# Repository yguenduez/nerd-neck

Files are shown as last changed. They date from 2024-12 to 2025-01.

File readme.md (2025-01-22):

# Nerd Neck on ESP32-S3

This small device will detect bad posture, if the person wearing this device has it attached to the back.

## Project structure

- [3dprint](3dprint): STL-Files for printing
- [images](images): All images used in the report or in this readme
- [nerd-neck](nerd-neck): Source code: Entry point for the program
- [utility](utility): Source code: Utility functions and the madgwick adapter
- [nerd-neck-report](nerd-neck-report): The [mdbook](https://github.com/rust-lang/mdBook) to render the report to pdf

## Outline

We read IMU data in a cycle. Every 50 milliseconds we receive IMU data.
As the IMU values drift, we need a filter(s): Those correct the drift integrated over time with sensor fusion
algorithms.

If the orientation of the device passes a certain threshold,
the device will start beeping for 2 seconds, notifying the person to rectify its position.
It will remain beeping, until the person corrected its position.

The whole device is a wearable, so it needs a battery (LiPo) and a 3d printed casing.

## TODOs

- [x] Calculate an angle to Z-Axis (with Filters), that can be used as "beep" input
- [x] ~~Do a calibration for the Gyro before starting (if not moving, gyro values should be 0).~~ (Filter already
  corrects offsets)
- [x] Write a little rust driver for the speaker, that controls it
- [x] On a configurable threshold - enable the trigger for the beep speaker
- [x] Apply a LiPo (3.7 Volts) battery adapter to the battery pins
- [x] Design 3d model for the casing to print
- [x] Print the casing
- [x] Assemble the parts
- [x] Write Report with Markdown
- [x] Slides with UniBas flavour

## IMU Drift

Gyroscope does drift, when integrated over time, so we need to correct those values with sensor fusion algorithms,
with other sensor values. Both IMUs we can use, also come with an accelerometer.
So we combine smooth short-them gyroscope data with long-term stability of accelerometer data.

Possible Filters:

- **Complementary filter** (simpler but effective for many use cases).
- **Madgwick filter** (a fast, quaternion-based algorithm for IMUs).
- **Mahony filter** (similar to Madgwick with some differences in accuracy and computation).
- **Kalman filter** (complex but precise, especially for combining multiple sensors).

**Note**: As we are only interested in the tilt of the IMU (diff angle to the vertical z-axis), we can neglect
the yaw angle (which would be corrected be the magnetometer, which we do not have).

So we can use either Madgwick or Mahony with only given accelerometer and gyro values.

### IMU Filter Implementation

There is already a [third party crate (ahrs-rs)](https://github.com/jmagnuson/ahrs-rs), that already implements both
Madgwick and Mahony filters
for both 6DoF and 9DoF IMUs.

A choice to be done is the filter gains, KI and KP for Mahony and Beta for Madgwick.

Some recommended beta values for the Madgwick Filter, where you have to choose
between responsiveness and stability:

| Drones/RC vehicles    | 0.1 - 0.3    | High dynamics, prioritize responsiveness.            |
|-----------------------|--------------|------------------------------------------------------|
| Robotics (general)    | 0.05 - 0.2   | Moderate dynamics, balance response and drift.       |
| Slow-motion systems   | 0.01 - 0.05  | Low dynamics, prioritize stability/noise rejection.  |
| Human motion tracking | 0.01 - 0.1   | Prioritize stability but allow small dynamic motion. |
| Static applications   | 0.001 - 0.01 | Low dynamics, focus on maximum stability.            |

TL;DR: We use the Madgwick filter with beta between 0.01 and 0.1. Currently, we use 0.1.
The paper for madgwick is [here](https://x-io.co.uk/downloads/madgwick_internal_report.pdf).

The Madgwick Feedback loop (from paper above):

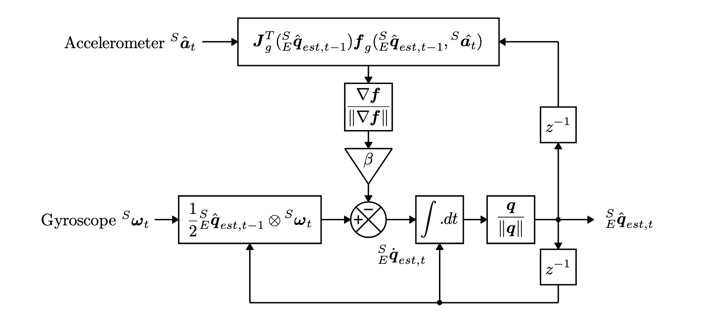
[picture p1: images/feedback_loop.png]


## IMU Sensors

We have several IMU Sensors

- [BMI160](https://www.dfrobot.com/product-1716.html)
- [MPU6050](https://learn.adafruit.com/mpu6050-6-dof-accelerometer-and-gyro/arduino)

Both can be addressed via a I2C-Bus.

## Software for the MPU6050

There is already a [MPU6050 crate](https://docs.rs/mpu6050/0.1.6/mpu6050/). It's usable with i2c.

## Software for the BMI160

There is already a [BMI160 create](https://docs.rs/bmi160/1.1.0/bmi160/). Also usable with i2c.

## I2C interface

This bus comes with a dataline (sda) and a line for the clock signal (scl).

You can connect several devices to the bus, like shown below.
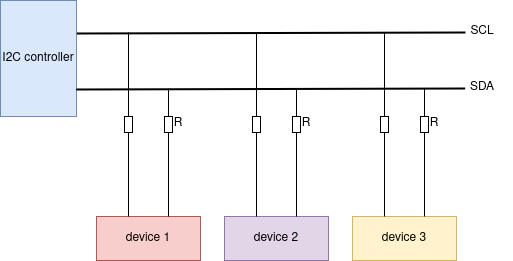
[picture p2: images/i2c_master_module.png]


Note from [espressif](https://docs.espressif.com/projects/esp-idf/en/v5.3.2/esp32s3/api-reference/peripherals/i2c.html):

> The frequency of SCL is influenced by both the pull-up resistor and the wire capacitance. Therefore, users are
> strongly recommended to choose appropriate pull-up resistors to make the frequency accurate. The recommended value for
> pull-up resistors usually ranges from 1K Ohms to 10K Ohms.
> Keep in mind that the higher the frequency, the smaller the pull-up resistor should be (but not less than 1 KOhms).
> Indeed, large resistors will decline the current, which will increase the clock switching time and reduce the
> frequency.
> We usually recommend a range of 2 KOhms to 5 KOhms, but users may also need to make some adjustments depending on
> their
> current draw requirements.

**TL;DR**: Use 2-10kOhm resistors as pull up resistors.
The higher the frequency, the lower the ohmage should be.

We use 4.7k Ohms as pull-up resistors.

## Pinouts of esp32s3 from Seeed

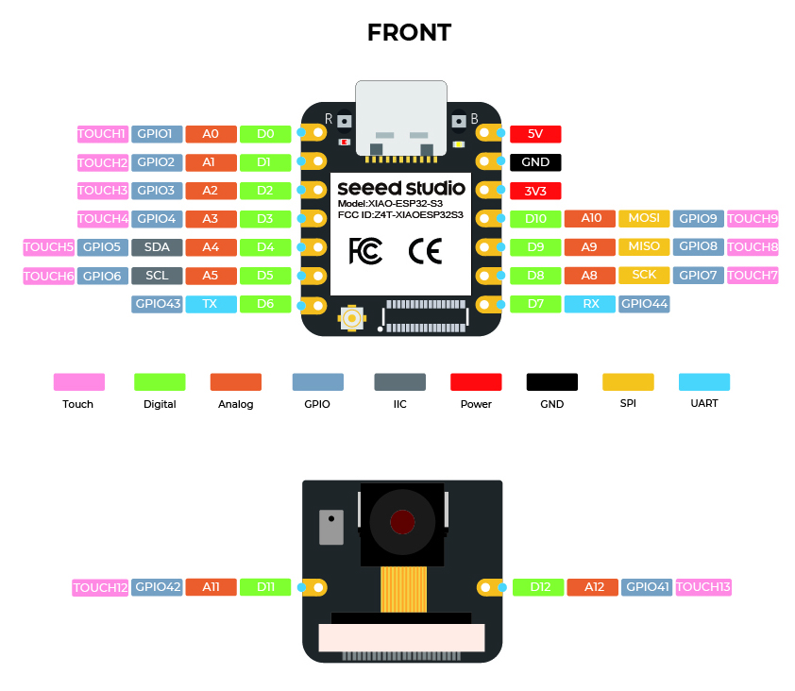
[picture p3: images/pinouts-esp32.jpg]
Pinouts


## Current Wiring

We have an i2c setup, where two 4.7k Ohm resistors are used as
pull up resistors. If scl/sda are off, both signals are pulled up to the logical 3.3 Volts (high). The IMU (on the
right)
will pull the signal down if needed.

Everything runs on the 3.3-volt level of the MCU.

The piezo speaker is connected to GPIO pin 7.
We use a 100 Ohms resistor to protect the GPIO from draining too much current.
So the piezo speaker drains at max 3.3v/100 Ohms = 33 mA of current.
It's powered with a 1 khz pwm signal, when triggered.

Below the fritzing image is demonstrating the wiring.
The parts are aliases though, we use different ones,
but the wiring is exactly the same.

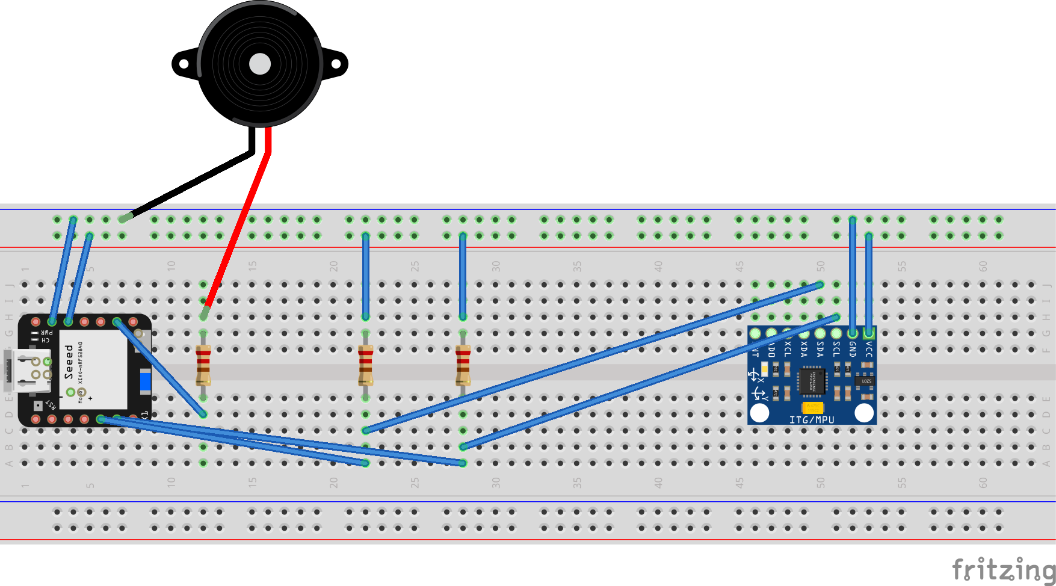
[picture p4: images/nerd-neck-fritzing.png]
fritzing


## Bill of Materials

Below all used Materials

### For the Breadboard Version

- MCU: Seeed xiao esp32s3, [link](https://wiki.seeedstudio.com/xiao_esp32s3_getting_started/)
- IMU: DF Robot BMI160 (6 DoF-IMU), [link](https://www.dfrobot.com/product-1716.html)
- 2x 4.7k Ohm Resistors as pull up resistors for the I2C connection
- 1x 100 Ohm Resistor for the piezo speaker
- Breadboard
- Active Piezo
  Buzzer, [link](https://www.bastelgarage.ch/piezo-buzzer-summer-aktiv?search=Piezo%20Buzzer%20Summer%20aktiv)
- Wires

### The Assembled (Battery powered Version)

- MCU: Seeed xiao esp32s3, [link](https://wiki.seeedstudio.com/xiao_esp32s3_getting_started/)
- IMU: DF Robot BMI160 (6 DoF-IMU), [link](https://www.dfrobot.com/product-1716.html)
- 2x 4.7k Ohm Resistors as pull up resistors for the I2C connection
- 1x 100 Ohm Resistor for the piezo speaker
- Active Piezo
  Buzzer, [link](https://www.bastelgarage.ch/piezo-buzzer-summer-aktiv?search=Piezo%20Buzzer%20Summer%20aktiv)
- Wires
- Battery: LiPo, 3.7 volts with
  1500mAh: [link](https://www.bastelgarage.ch/lipo-akku-1500mah-jst-2-0-lithium-ion-polymer?search=LiPo%20Akku%201500mAh%20JST%202.0%20%2F%20Lithium%20Ion%20Polymer)
- JST-PH crimp plugs and sockets (To not directly solder the battery to the
  MCU), [link](https://www.bastelgarage.ch/jst-ph-crimp-stecker-und-buchsen-2mm-set-40-stuck)

## Building and flashing

### Prerequisites

Install all the depenendencies:

- Install [Rust](https://www.rust-lang.org/tools/install)
- Install esp tooling
    - `cargo install espup espflash`
    - `espup install`

### Building/Flashing

Then go into the `nerd-neck` directory and
`source ~/export-esp.h` (generated from `espup install`).

To build and flash the firmware to the device,
just run `cargo run --release`.

# Casing

## Requirements

The casing must include

- a LiPo battery (3.7 Volts),
  e.g. [this one](https://www.bastelgarage.ch/lipo-akku-1500mah-jst-2-0-lithium-ion-polymer?search=lipo) (52x42x5mm),
- the BMI160 IMU from DFRobots with dimensions 23x27mm as well as the
- the esp32s3 from seeed with dimensions ~20x25mm. Also having access to its usb-c port.
- the piezo buzzer with its dimensions, e.g. [this one](https://www.bastelgarage.ch/piezo-buzzer-summer-aktiv) (12mm)

As the casing will be quite flat, we have on one layer the flat LiPo battery on the bottom
and on the other layer the IMU, the MCU and the piezo buzzer. The wiring will be in between
those two.

Also: It should be possible to exchange all parts.

The casing will have the dimension of 56x46x10mm, so we
have a will thickness of 1mm on each side.

## Designs with Freecad

All below versions were designed with [FreeCad](https://www.freecad.org/), an open-source
CAD Software running on all major platforms (Mac, Linux and Windows).

### Version 0.1

The first design looks like this:

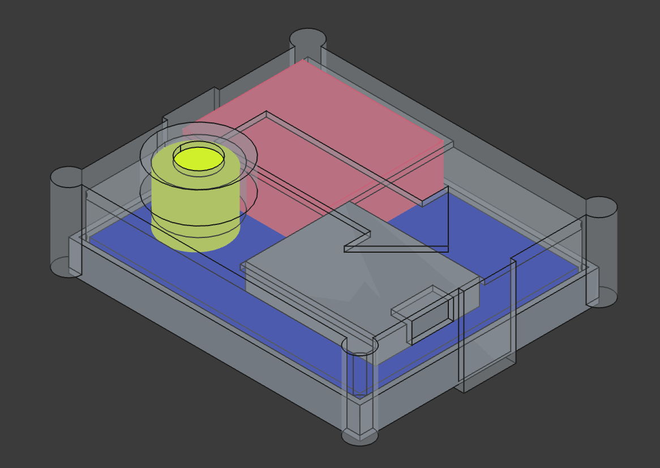
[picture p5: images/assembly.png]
assembly


Where the parts are the following:

- Red: the IMU
- Grey: Esp32s3
- Yellow: Piezo speaker
- Blue: the LiPo battery

The casing itself consists of a bottom and a top casing.
The bottom casing houses the battery.
The top casing holds the rest. Both parts are designed that way, that the
bottom half slips into the top half and snaps in.

The whole casing has the following dimensions: 56x46x15mm (circle on top for the buzzer has hight of 6mm)

### Version 0.2

Changes to V0.1:

- To make the design more 3D-print friendly, there is no exterior for the buzzer any more.
  The downside is,
  the buzzer is exposed a bit.
- The hole for the usb got bigger, as it did not go through without drilling.
- The two holders, that hold the bottom part, got 1mm longer, as the bottom part did not fit in.

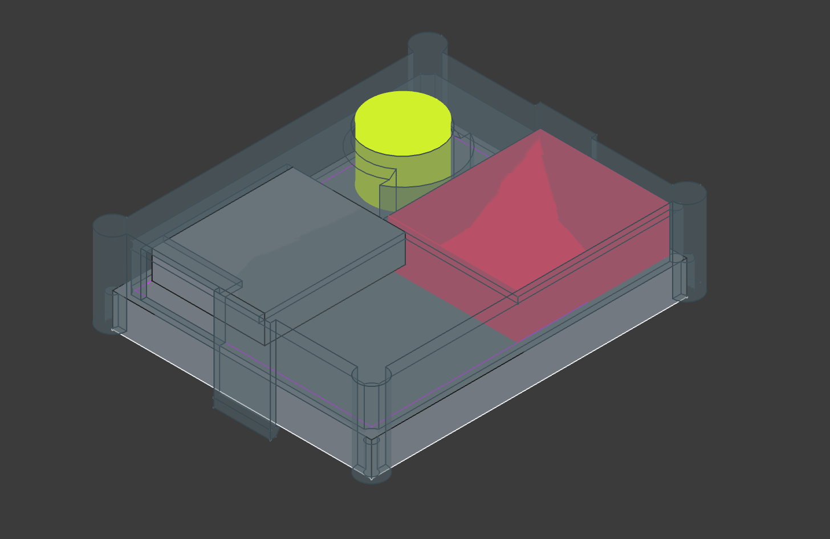
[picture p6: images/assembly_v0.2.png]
assmbly


### Version 0.3

Changes to V0.2:

- We thickened the holders by increasing their thickness from 1 mm to 2 mm.
- We resized the hole for the usb-c port.
- Decrease the height of the piezo buzzer holder, as the battery would not fit
- Decrease diameter of piezo buzzer hole from 13 mm to 12.3 mm

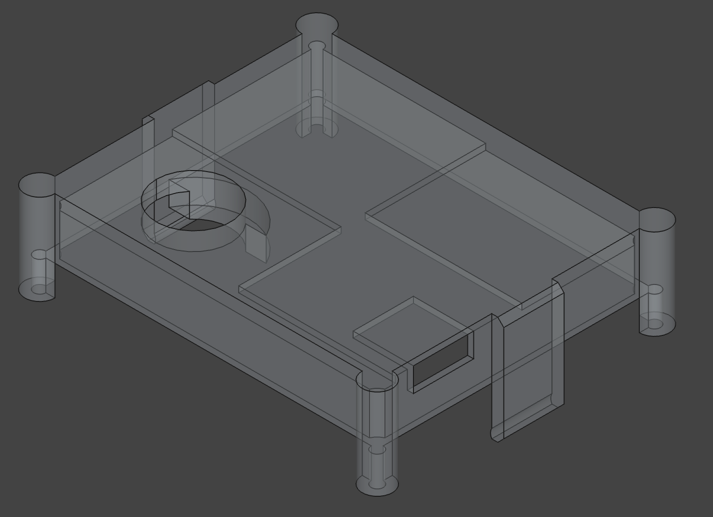
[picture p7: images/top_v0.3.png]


### Version 0.4

Changes to V0.3:

Instead of having a top and a bottom, the bottom part can now slide into the top part.
As such, we do not need any clips, to hold the bottom port. Only with gravity
the casing holds. The bottom part must be attached to a t-shirt in the end, as this will
hold the complete construction.

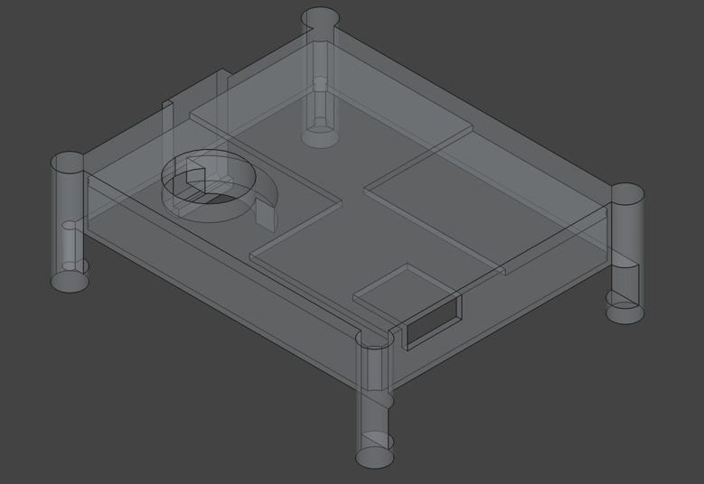
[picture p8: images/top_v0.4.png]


### Press-fit (Version 0.5)

Instead of sliding and clipping, we also tried a pressfit version.
The basic idea is that both parts, you want to connect do not perfectly fit to one another.
Instead they have an overlay, so you have to press them into each other.

The shear friction between those parts is enough, so they stick together.

The obvious pros. The parts are much easier to design, as you can see below (and compare them with the previous version)

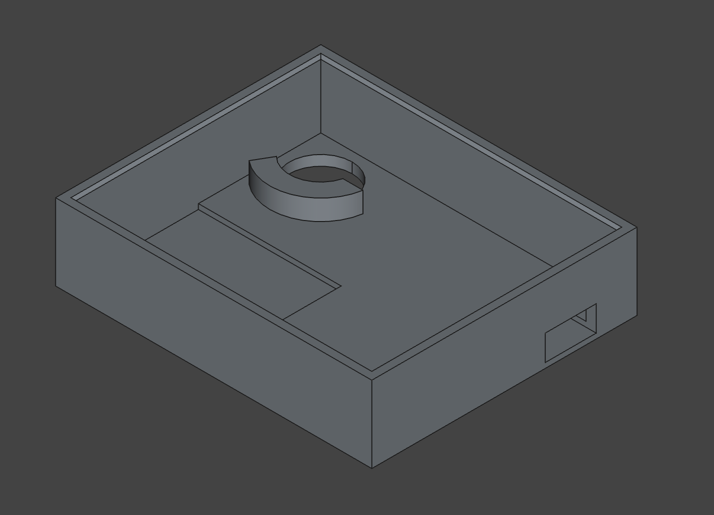
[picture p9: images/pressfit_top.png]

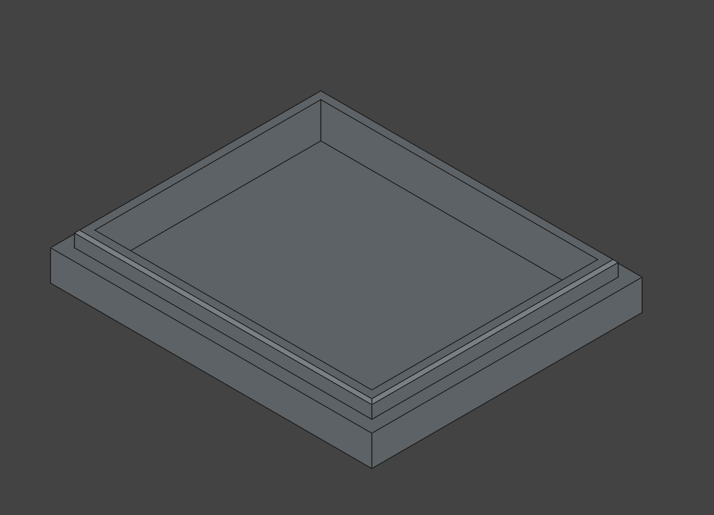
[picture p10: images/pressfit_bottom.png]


## The press fit is the final version

Printed, it looks like this:

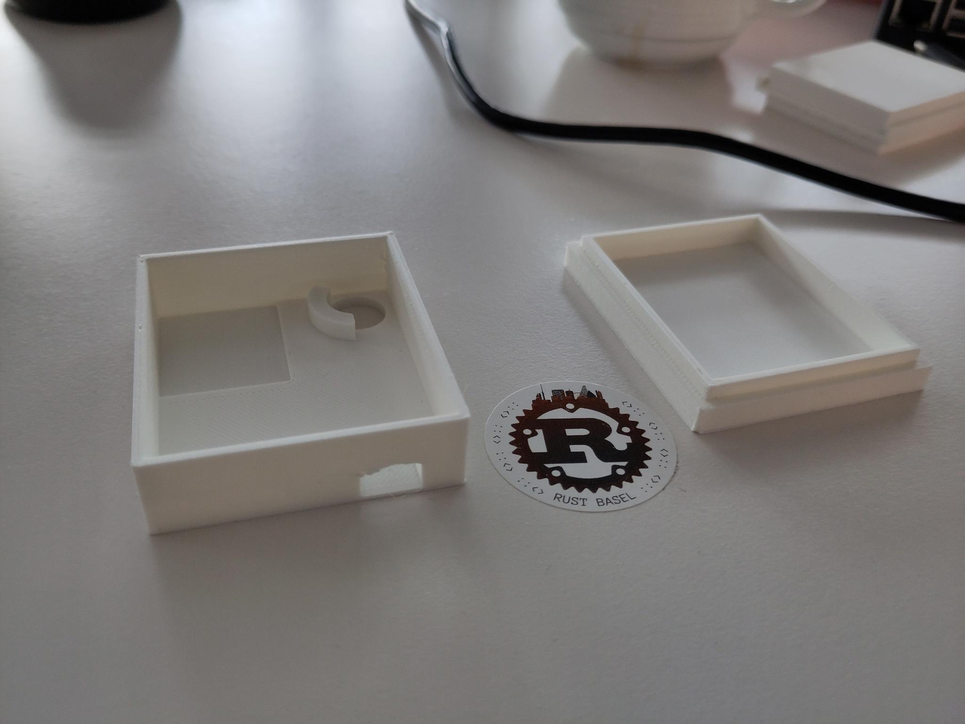
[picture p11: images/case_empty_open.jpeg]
casing_open

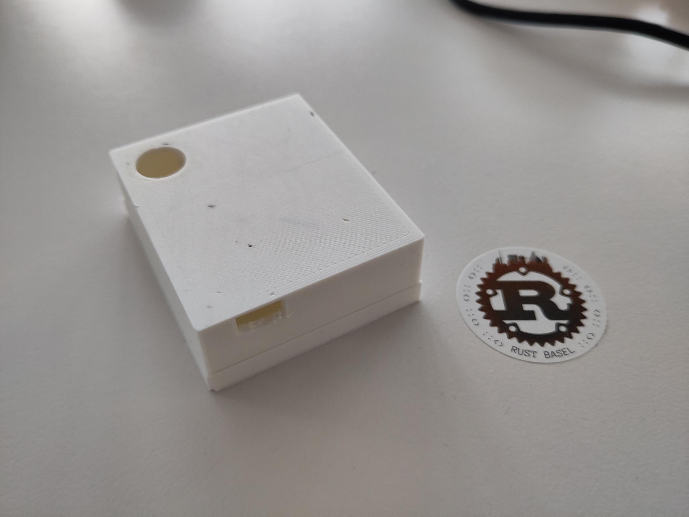
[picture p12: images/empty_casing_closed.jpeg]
casing_open


# Assembled Prototype

Below images of the assembled prototype, case opened and case closed

Opened:

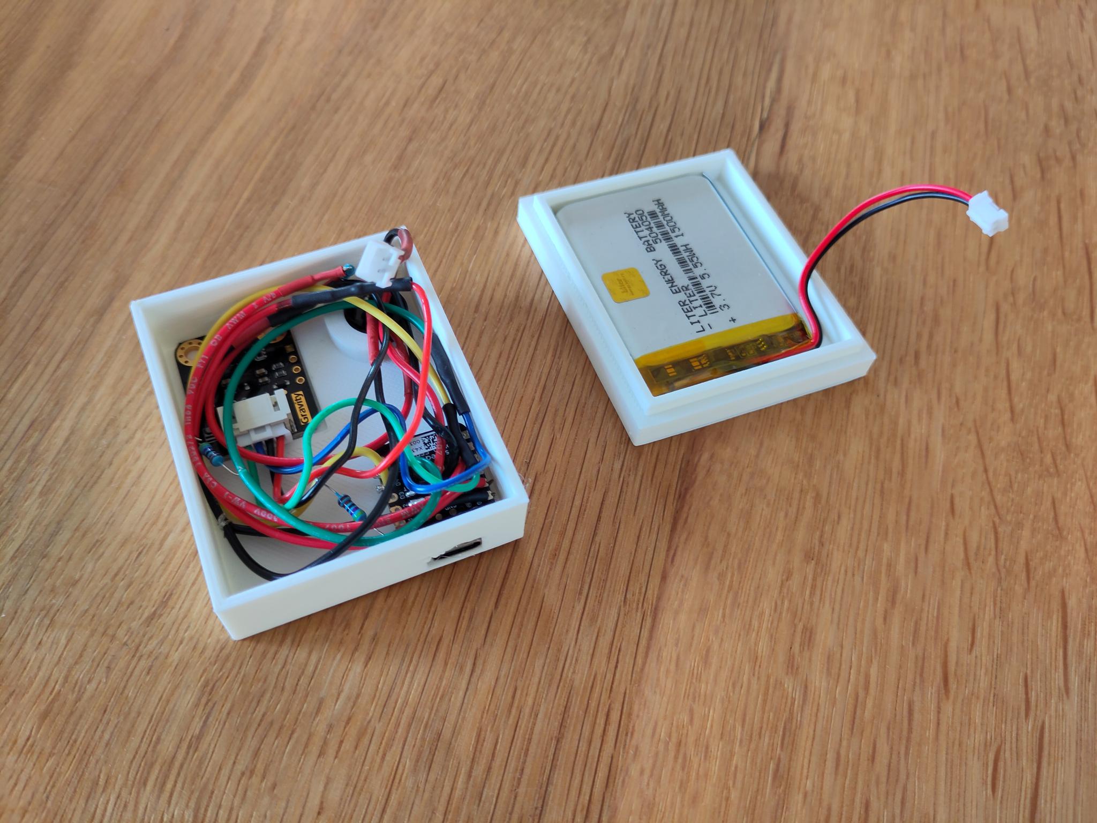
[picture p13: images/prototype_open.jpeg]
prototype_open


Closed:

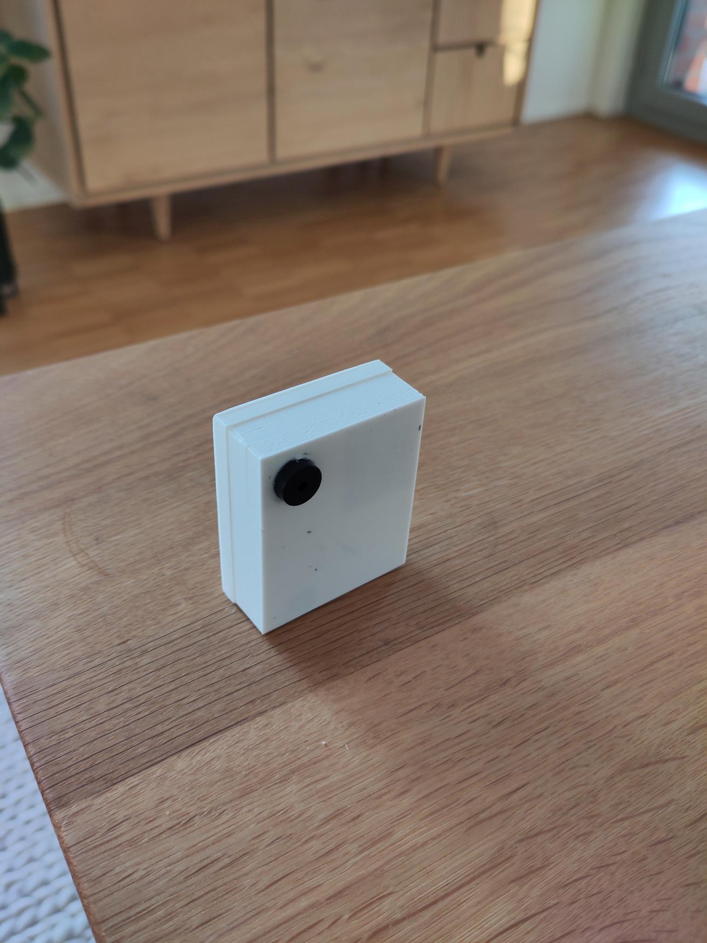
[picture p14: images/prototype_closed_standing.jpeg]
prototype_standing


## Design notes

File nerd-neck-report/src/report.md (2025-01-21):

# Nerd Neck - A wearable health device

## Context

This is the report for the nerd neck device. An embedded project for the lecture _Computer Architecture_ at the
University Basel for
the semester 2024.

Date: January 21st 2025

Student: Yasin Gündüz

# Abstract

In today's office work people are sitting much, which results in several health issues, like back pain
or chronicle bad postures. One of these is called "nerd neck", where the head protrudes forward from the shoulders.
This project is an effort to help people maintain a good posture while sitting
or standing, to decrease health issues originated by bad posture habits.

The nerd neck device is a 3d-printed wearable device where the device is
attached to a persons back and tracks the back's orientation in regards the gravity's axis.
Using an ESP32 and programmed in Rust, an inertial measurement unit together with a sensor fusion filter is
efficiently detecting the person's posture. When a bad posture is detected, a buzzer will notify the person to correct
the posture.

# Introduction

Office workers, or programmers, tend to have a bad posture in front of their laptops, or working at
desks. When exposed too long to a bad posture, this can result in several health issues. Back pain is just one example
of this.
There are already countermeasures to fight bad postures. For example ergonomic trainings for office
workers are carried out, to make working in office jobs healthier.

The approach this project is following is a bit different. Instead of proactive trainings,
the outcome of this project should be to react to a bad posture of a person and a user
should be notified when having a bad posture.

As this project should be wearable, it means the device must be battery powered. Also, as a person
is wearing this device, the form factor of the device should not be big, so it is for example
attachable to a person's back.

The project is already restricted to be as small as possible and battery powered. Being battery powered,
it also means it is not allowed to draw much current to remain active for as long as possible.

Moreover, it must track the posture of a person to be able to react to a bad posture.
The person must also be notified when being in a bad posture.

In the following sections, I will describe how I solved above goals.

# Methodology

The methodology is separated in a hardware section and a software section. In the hardware section,
we will look at the components, the wiring between them and the 3d printed casing, that houses them.
Afterwards, we will look at how software is designed and how it supplements the project goals to get
the orientation of the device.

## Hardware

### Components and Wiring

To be as small as possible, the esp32s3 from seeed xiao, a microcontroller unit (MCU), is used.
It comes with a small form factor and can be directly
soldered to a Lithium-Polymer (LiPo) battery for which it has an integrated circuit to load the battery.
This already solves the battery-driven goal of this project.

To detect the person's bad posture the orientation of a person's back is measured. Therefore,
we use an inertial measurement unit (IMU), that gives us the orientation information with its gyroscope values.
The IMU is connected via an inter-integrated-circuit (I2C), a common serial communication protocol,
to communicate with the MCU.

When reaching a certain orientation (i.e. a bad posture), an active buzzer is attached to one of the
general purpose output/input (GPIO) pin of the MCU.

Below, you can see the wiring of the breadboard version of the device. The I2C is connected to the GPIO pins
5 and 6. To make the I2C work, it is necessary to have pull-up resistors,
that pull the signal to the MCU's high logical voltage (3.3 volts). The IMU itself can only pull the signal down
to the logical zero volts.
This is what I had to learn during several hours of debugging. Common I2C resistor values of 4.7k Ohms are used.

The resistor for the buzzer is to protect the MCU's GPIO from overdrawing current of the buzzer. There a 100 Ohms
resistor is used.

<div align="center">
Fritzing Image
</div>

For a complete list of all the components, have a look at the reference section.

### 3d Printed Casing

As the device should be wearable, all the components from above need to be housed.
Therefore, a 3d printed casing was designed. It consists of a bottom shell and
top shell, that can be connected to one another, to close the housing.

As the LiPo battery is quite flat, the battery is housed in the bottom part, whereas the
top shell is housing the MCU, the buzzer as well as the IMU.

You can see both parts in the pictures below, without and with the components in it.

<div style="display: flex; justify-content: space-evenly; width: 100%;">
  Fritzing Image
  Fritzing Image
</div>

There were a lot of problems with the initial designs (you can see them at
the [nerd-neck project](https://github.com/yguenduez/nerd-neck)).
First, it was tried
to create a design that allows the bottom shell to be snapped in the top shell of the housing to close
it.

However, the small snapping elements always broke because they have been too thin and therefore quite weak.
In a second iteration, it was tried to make the housing slideable. Meaning, we can slide the bottom (battery part) into
the top shell. With this design, the housing was just too big, compared to the inner volume the components are housed
in.

In the end, after already four design iterations, a small tip from a colleague helped. He mentioned that I should
use a so-called "pressfit" version. This means the two parts do not fit perfectly into one another, so you have to press
them into each other. The friction alone keeps both parts together. As an immediate consequence, the housing got much
simpler to design—and also to use.

# Software

The firmware for the esp32s3 is written with Rust. [Espressif](https://www.espressif.com/), the creators of the esp32
family created a lot of tooling in Rust
for their MCUs. With one line of a command, you can build and flash the firmware directly onto the esp32 from any host
system (in this case MacOS or Windows 11) via usb-c. This project makes also use of the
[esp_hal](https://github.com/esp-rs/esp-hal). A hardware abstraction layer for the esp32 family.

The only downside to Rust in the embedded world is that it is quite new. Tutorials and HowTos
were already outdated when reading them. Generally, you have to stick to the latest documentation,
that comes with a library you use.
Trying to use ChatGPT for programming was useless, as the recommended APIs were already outdated. And most
of the APIs had breaking changes in them.

## Architecture

In software, the tracking of a person's pose and the notification of a bad posture are separated. Therefore,
there are two concurrent running tasks, namely the IMU polling task and the notification task, which you can see
in the below flowchart diagram.

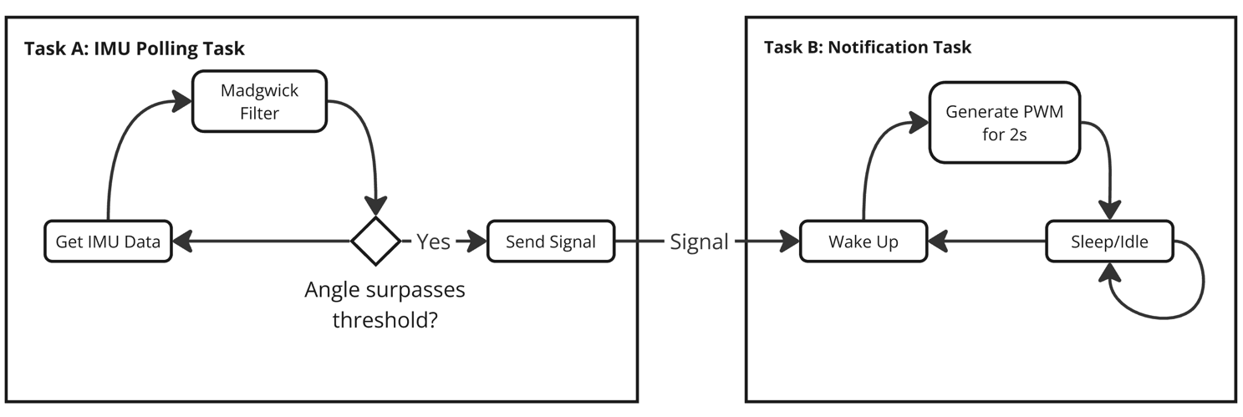
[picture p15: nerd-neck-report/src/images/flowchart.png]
flowchart


The IMU polling task gets the angular velocities,
as well as the acceleration data from the IMU every 50 milliseconds.
Directly after, both vectors are given to the Madgwick filter adapter, to correct the errors of the IMU
data.

From our filter we receive a quaternion, which describes the current orientation of our device.
At the end of the loop cycle of the IMU polling task, we check if the device's orientation to the z-Axis (direction of
gravity) surpasses a threshold.
Namely, if the angle between the device and the gravity's direction
is greater than 22.5 degrees, we send a signal to the notification task, to wake it up.

When the notification task is awakened, we generate a PWM signal of 1kHZ for 2 seconds and put the notification task
back to sleep to save power afterwards.

When the PWM signal is on, an active buzzer generates sound.
We manually generate the PWM signal
by setting a GPIO pin to high, wait 500 microseconds and set the GPIO pin
to low again. While the Buzzer is active, any further signals from the first task are ignored.

It is important to note that the asynchronous rust framework [embassy](https://embassy.dev/) for embedded
systems allows the tasks to be concurrent. On high level, it acts as a scheduler for our embedded device, putting
tasks to sleep, and waking them up, when needed.

## Sensor Fusion

### Choosing a Filter

IMU angular velocities cannot just be integrated over time, as those values
are error-prone. One will receive a so-called IMU-Drift, where the errors are also integrated over time.

To solve this issue, there are already several filters at hand, that could be
used for the project:

- Kalman Filter
- Mahony Filter
- Complementary Filter
- etc.

It has been a spoilt for choice. The filter chosen, usually used for an embedded device, is the Madgwick Filter.
Additionally, there has been an open-source library with its implementation at
hand ([ahrs-rs](https://github.com/jmagnuson/ahrs-rs)) that is used.

### Madgwick Filter

The Madgwick filter ([paper](https://x-io.co.uk/downloads/madgwick_internal_report.pdf)) is a sensor fusion algorithm
by Sebastian Madgwick,
that is suited well for embedded devices due to its efficiency.

It integrates the angular velocities, by integration of the quaternion derivatives over time.
As integration of angular velocities from an IMU is prone to drift, the madgwick filter uses
the earth's gravity field as a reference direction to compensate for the IMU
drift
([source here](https://ahrs.readthedocs.io/en/latest/filters/madgwick.html#orientation-as-solution-of-gradient-descent)).

The Madgwick filter has one parameter you need to adjust.
It is called the filter gain beta.

When picking the right value for beta, there is a trade-off between the stability
of the resulting orientation and its response. For example, for drones which
have to react fast, the Madgwick Filter is optimised for high responsiveness by using a high beta value.
On almost static, or human motion tracking, the filter is optimised for stable output using lower beta values.

A value of 0.1 is used (This is the default value chosen by the library that is used),
showed already a good trade-off between responsiveness and stability for the application.

# Closing

Doing this project was really rewarding. On the one hand, you could integrate
already known concepts from software engineering. On the other hand you could integrate
knowledge from hobby projects like 3d printing.
You could even learn something completely new, which was Rust on the embedded side and
soldering for me.

In the end, I created a battery-driven, wearable device, that can track a posture
and notify a person when having a bad posture and thus can help
people foster a healthier lifestyle.

Below the image of the assembled device

<div align="center">
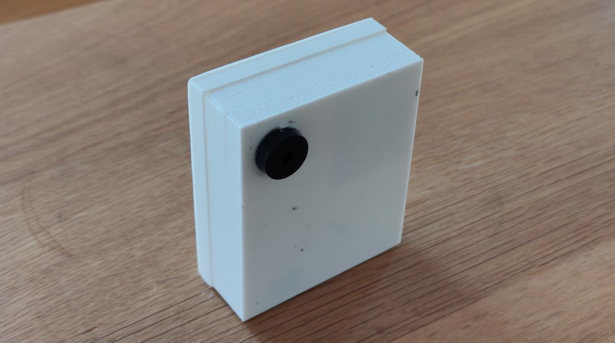
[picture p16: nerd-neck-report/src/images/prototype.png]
Finished prototype

</div>

But of course, there are several points, that can be improved, which I describe in the following section.

## Improvements

The first thing, that can be improved, is the battery management. The MCU can load the battery,
but there is no information about the current charge of the battery. This is potentially dangerous,
as the LiPo could be drawn empty.

Also, being new at soldering, the cable management could be improved a lot. Maybe adapter solutions could be used
instead of soldering connections.

Furthermore, it would have been interesting to fine tune to the beta value of the Madgwick filter, which I did not do.

In the below list, more improvements are added:

- Using an MCU with an integrated IMU: For example,
  the [Seeed xiao nRF sense](https://www.seeedstudio.com/Seeed-XIAO-BLE-Sense-nRF52840-p-5253.html) comes with an
  integrated IMU. With this, the I2C connection could be made obsolete.
- Smaller LiPo Battery, making the device smaller: The battery is quite oversized for such a small project.
- The MCU supports Bluetooth. One could connect the device via bluetooth to a
  smartphone.

# References

The project itself is open-sourced at [https://github.com/yguenduez/nerd-neck](https://github.com/yguenduez/nerd-neck).
The code, stl files for printing and more documentation (on e.g. how to build and flash the project), can be found
there.

## Content

- [Madgwick Paper](https://courses.cs.washington.edu/courses/cse466/14au/labs/l4/madgwick_internal_report.pdf)
- [Sharing Data amongst asynchronous tasks in embassy](https://dev.to/theembeddedrustacean/sharing-data-among-tasks-in-rust-embassy-synchronization-primitives-59hk)
- [Discussion on Madgwick Beta Value](https://stackoverflow.com/a/47772311/7585591)
- [Documentation for the esp32s3 from seeed xiao](https://wiki.seeedstudio.com/xiao_esp32s3_getting_started/)
- [Rust library documentations: docs.rs](https://docs.rs/)

## Use of open-source libraries and frameworks

This project makes use of several open source libraries:

- The [esp_hal](https://github.com/esp-rs/esp-hal), an esp hardware abstraction layer for Rust.
- [Embassy](https://embassy.dev/) is used. An asynchronous runtime for embedded systems in Rust.
- For the inertial measurement unit (IMU), the [bmi160-rs](https://github.com/eldruin/bmi160-rs) is used.
- For the Madgwick filter, I used [ahrs-rs](https://github.com/jmagnuson/ahrs-rs).
- [nalgebra](https://github.com/dimforge/nalgebra) is used to work with quaternions, calculating angles.

## Bill of Materials

- a small microcontroller unit (MCU), an esp32s3 from xiao seeed, which has a small form
  factor. [Link](https://www.bastelgarage.ch/seeed-studio-xiao-esp32-s3-1-2809?search=esp32s3%20xiao%20seeed).
- an inertial measurement unit (IMU), that can measure acceleration and the angular velocity with a
  gyroscope. [Link](https://www.bastelgarage.ch/gravity-i2c-bmi160-6-axis-motion-sensor-with-gyroscope?search=bmi160)
- a small lithium polymer (LiPo) battery, to power the wearable
  device. [Link](https://www.bastelgarage.ch/solar-lipo-1-105/lipo-battery-1500mah-jst-2-0-lithium-ion-polymer).
- a small beeper/buzzer to notify the person about a bad
  posture. [Link](https://www.bastelgarage.ch/piezo-buzzer-summer-active?search=active%20buzzer)
- 2x 4.7k Ohm Resistors for the i2c connection.
- 1x 100 Ohm Resistor for the GPIO pin 7 for overdrawing protection
- Wires to connect the components by soldering
- JST-PH crimp plugs and sockets (To not directly solder the battery to the
  MCU), [link](https://www.bastelgarage.ch/jst-ph-crimp-stecker-und-buchsen-2mm-set-40-stuck)

# Disclaimer

OpenAI GPT-4o was trying to be used at the beginning of the project. But no generated code was used, as
the suggested API calls either did not exist (were hallucinated), or were just completely outdated.
In the end, library documentations at [docs.rs](https://docs.rs/) were the only valuable source of truth.

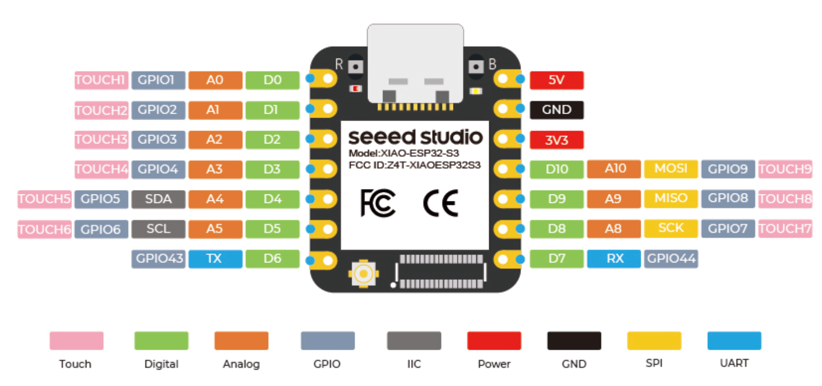
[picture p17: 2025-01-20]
images/pinout.png

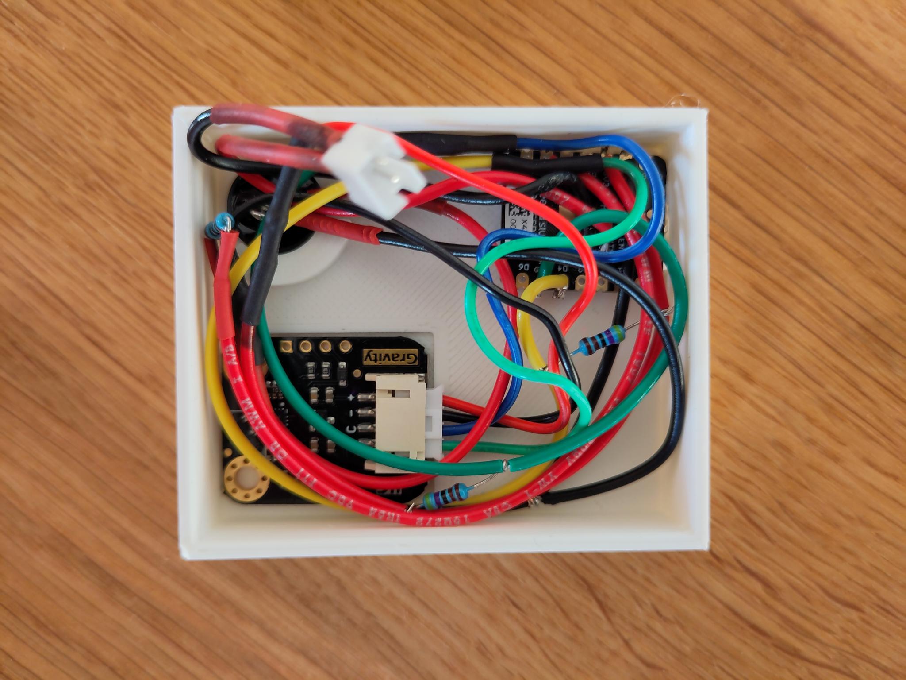
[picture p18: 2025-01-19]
images/cable_chaos.jpeg

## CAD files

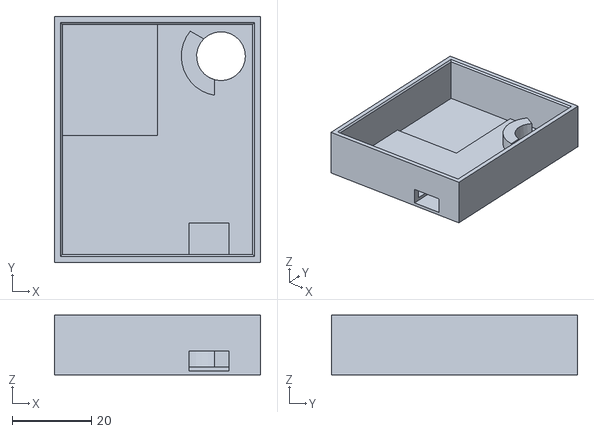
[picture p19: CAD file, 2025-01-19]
3dprint/Pressfit-Top.stl
52.0 x 62.0 x 15.0

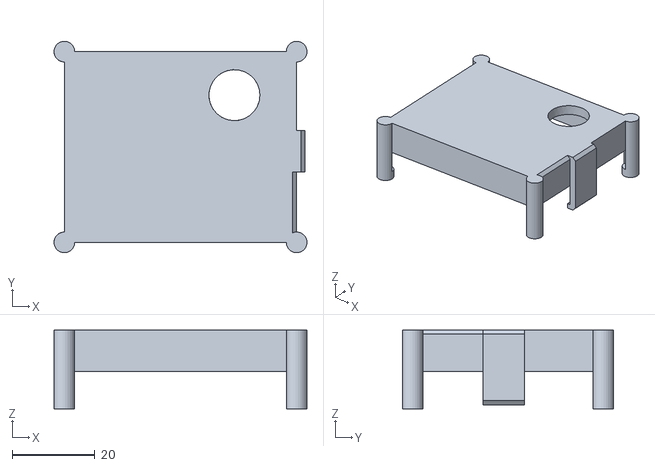
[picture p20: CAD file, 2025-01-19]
3dprint/nerd-neck-casing-4.0-Top.stl
61.0 x 51.0 x 19.0

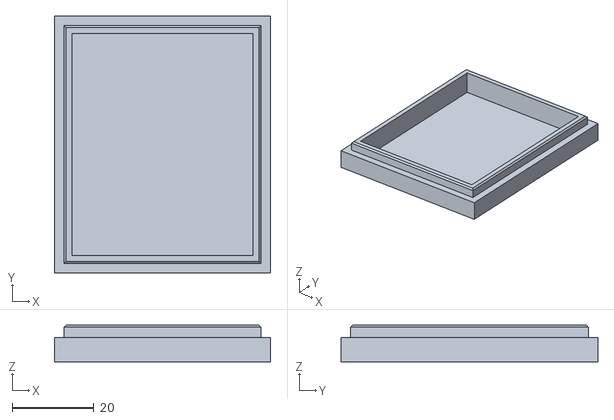
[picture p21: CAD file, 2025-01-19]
3dprint/Pressfit-Bottom.stl
53.0 x 63.0 x 9.00

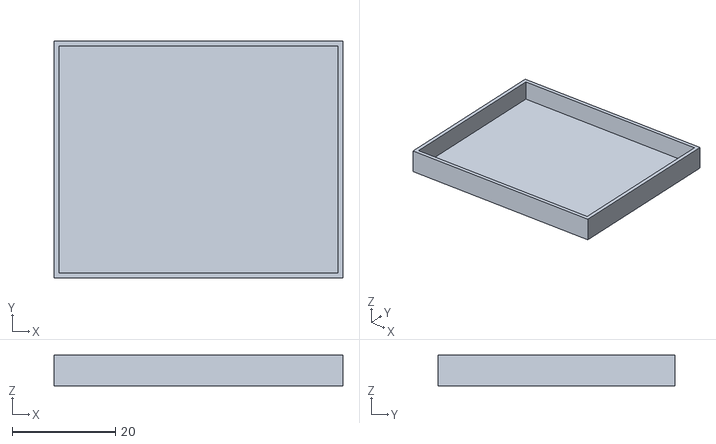
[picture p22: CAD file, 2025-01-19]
3dprint/nerd-neck-casing-4.0-Bottom.stl
56.0 x 46.0 x 6.00

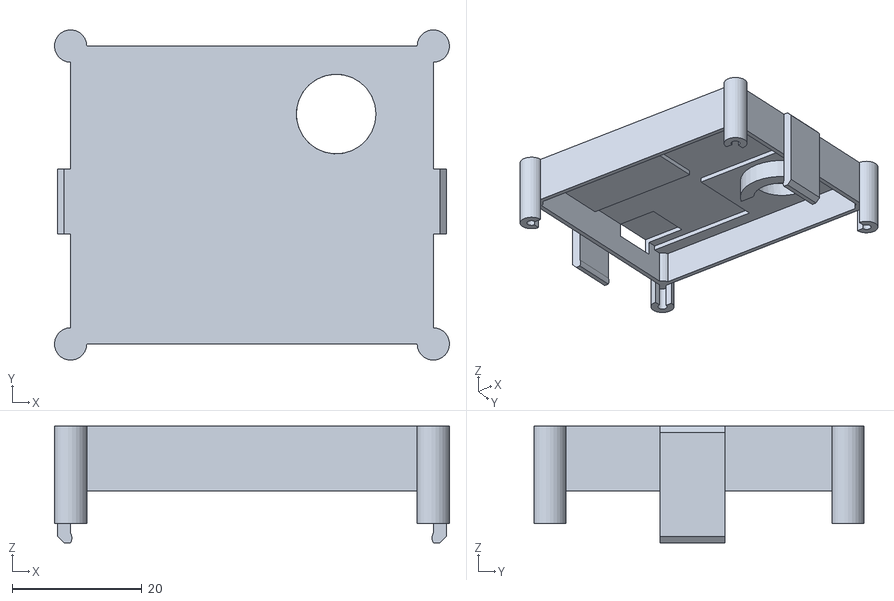
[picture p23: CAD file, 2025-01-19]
3dprint/nerd-neck-casing-3.0-Top.stl
61.0 x 51.0 x 18.0

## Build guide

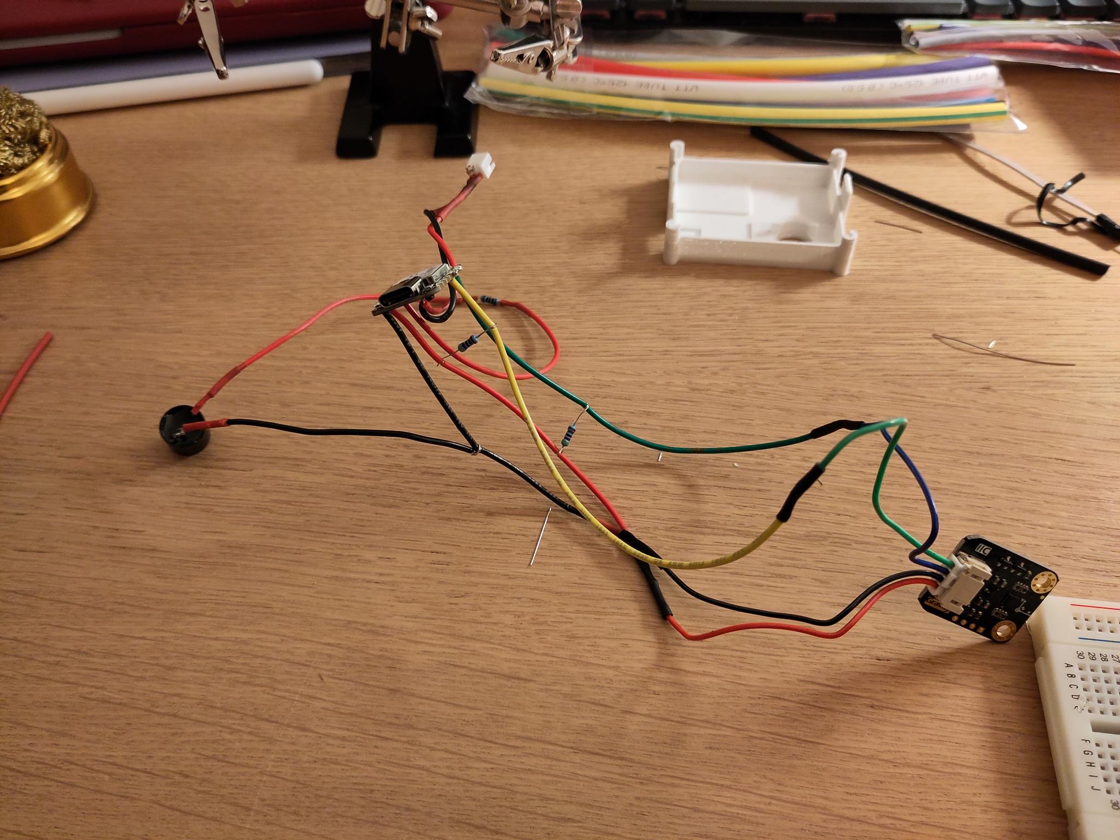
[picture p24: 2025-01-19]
images/soldered_prototype.jpeg

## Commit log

2024-12-21 hello world with template for esp32-s3
2024-12-24 add esp32s3 pinouts
2024-12-26 readme: add simple wiring from fritzing
2024-12-26 unfinished moving median filter and mahony c implementation
2024-12-26 run at 50Hz
2024-12-27 add first draft of housing
2024-12-27 readme: consequences of assembly for IMU threshold for notifying
2025-01-08 add version housing v0.2
2025-01-09 casing printed, but needs a v0.3
2025-01-19 add stl models
    [nerd-neck-casing-3.0-Bottom.stl, nerd-neck-casing-3.0-Top.stl]
2025-01-19 3dprint: remove not needed hole
    [nerd-neck-casing-3.0-Top.stl]
2025-01-19 3dprint: add version 04
    [nerd-neck-casing-4.0-Bottom.stl, nerd-neck-casing-4.0-Top.stl]
2025-01-19 3dprint: add pressfit version
    [Pressfit-Bottom.stl, Pressfit-Top.stl]
2025-01-19 readme: add finished prototype
2025-01-20 wip: add flowchart
2025-01-20 add image of the 3d printed part
2025-01-22 readme: current values
